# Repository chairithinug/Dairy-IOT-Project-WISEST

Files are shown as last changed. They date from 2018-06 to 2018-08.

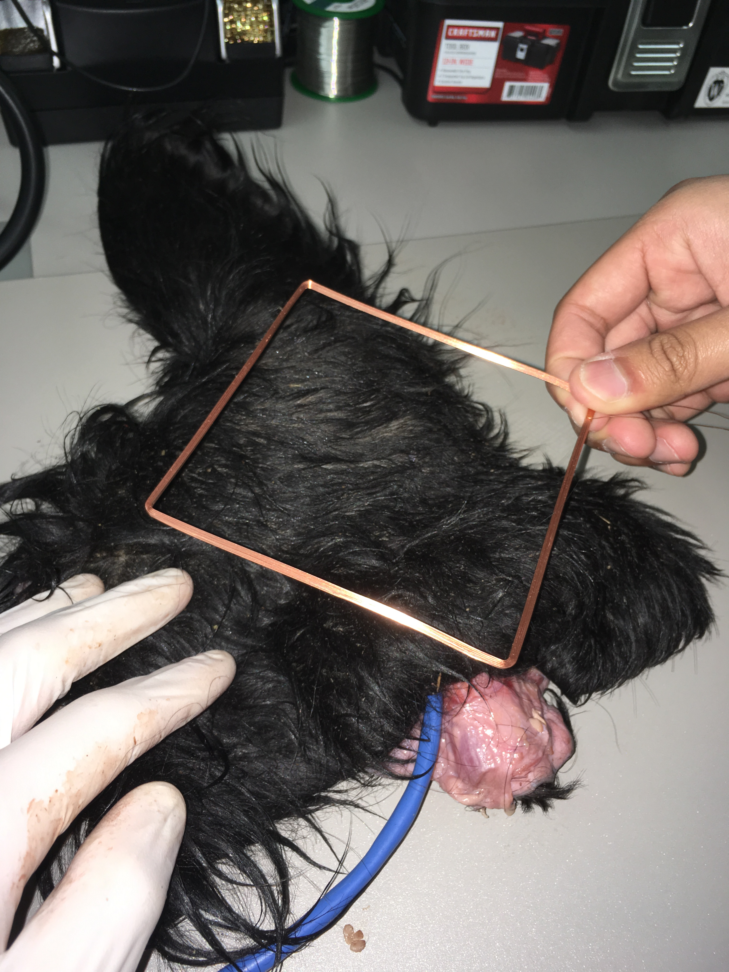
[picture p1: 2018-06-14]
Extras/IMG-1292.JPG

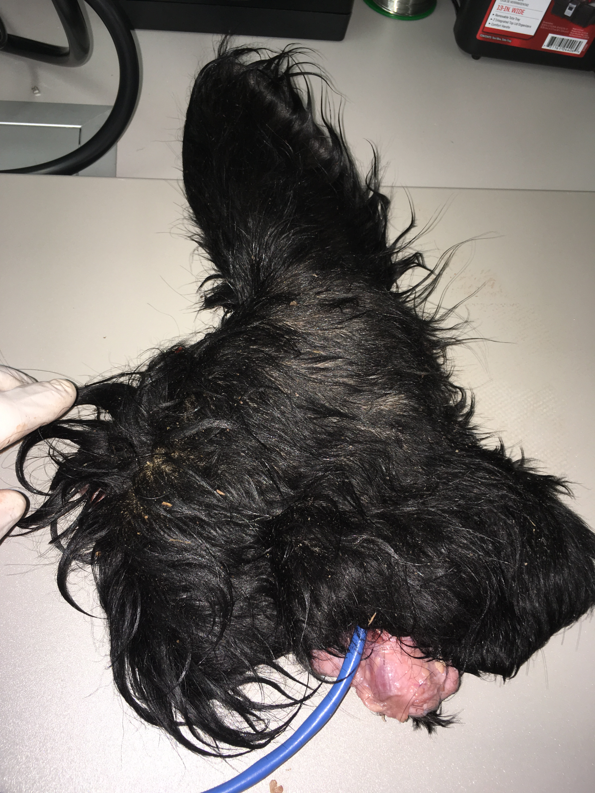
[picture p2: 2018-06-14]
Extras/IMG-1290.JPG

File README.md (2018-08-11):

# Overview
This is a private repository for my project at WISEST lab during Summer 2018 as an undergraduate research assistant. This project is a dairy IoT, using chiefly Arduino (C++/C) and MATLAB. MATLAB is responsible for gathering data from experiments and finding calibration coefficients. Arduino programs a microcontroller board. The goal is to monitor the core temperature of livestock and to wirelessly send the data through the internet.

# Components used
1. Adafruit Feather M0 LoRa MCU x2
2. ESP8266 WiFi Module
3. Priority1 RFIDRW-E-TTL Reader with an antenna
4. Bio temperature sensors
5. UBBL24-Fl-TH 7.4V 4800 mAh Batteries
6. MCP1702-3303 LDO
7. VN4012 NMOS
8. 1 uF Capacitors
9. Clipping Diodes (not used previously but recommended on RX-TX)
10. Wires
11. Prototype board
12. Header pins

# Useful electronic devices
1. Soldering station
2. Power supply
3. DMM
4. Oscilloscope

# Softwares used
1. Arduino IDE
2. Matlab R2018a
3. Altium Designer
4. Git
5. Microsoft Office
6. Google Chrome

# Libraries used
1. RH_RF95 LoRa library
2. RTCZero Timer/Low power library
3. SPI (may not actually needed)

# Codes (inside Codes folder)
1. LoRa_RX_Multi		HUB's code
2. LoRa_TX_RTC_V2		Device's code
3. LoRa_TX_NMOS			Debugging code without a sleep mode
4. Online_Matlab_Code	Thingspeak code

# Schematics
1. High-level Schematics
2. Detailed Schematics of a Hub
3. Detailed Schematics of a Device

# Useful resources
1. ESP8266 AT Command
2. Adafruit Feather M0 LoRa schematics
3. Datasheets of components
4. Some files in Extras folder

# TODO-Issue list
1. Change a number of devices connected to the hub.
2. Change a period of the reading.
3. Collision handling could be better by echoing some parts of data sent from a device to a hub back to the device.
4. Floating pin on a reader when NMOS creates an open circuit will need to be addressed. Now the current likely goes through RX-TX, which is not good.
5. There is still a grounding problem with a device and it can pick up a wrong part of data to be sent or receive a wrong data.
6. Sending all reading data to the hub might be a good idea than processing some of them on a device. This comes at a cost of power consumption.
7. Make a solid protocol between devices and a hub and across all devices.

# Words of caution when integrating parts
1. Do not connect V+ and GND of a battery. It could explode.
2. Be careful when using a DMM. Do not let a probe touch any 2 pins. This creates a short circuit.
3. Unplug or turn off a power supply first before removing any components.
4. MCU and IC are sensitive parts. Be especially careful when connecting them and notice the Vin of them.
5. When doing a hardware debugging, start at which the problem most likely happens.

# Setting up a device
1. Change period, LoRa signal power, and other variables if needed.
2. Program a device. Double-push the reset button and wait for a LED to blink, if needed.
3. Be careful when messing with Sleep mode/Standby mode of MCU. It might brick the device. 
4. In a standby mode (sleep mode), you cannot really use serial communication with a PC since the sleep mode cut the communication.
5. If needed, use LoRa_TX_NMOS to debug a device. That program does not have a sleep mode in it, while still printing a reading through a serial communication.

# Setting up a hub
1. Change a number of devices, sample per wake or other variables if needed.
2. Program a hub.
3. The LED blinks every time a hub gets any inputs.

# Setting up a Thingspeak.com
1. Create a channel that takes inputs from a hub.
2. Read data using readAPIkey and channelID.
3. Use Matlab Analysis to analyze the data.
4. Post data to a different channel using writeAPIkey and channelID.
5. Edit charts and set public view.
6. If needed, data can be exported in a CSV file.

# Charging batteries guide
1. Use a power supply and set a constant voltage (max voltage) and a constant current (1 A recommended)
2. Do not a power supply directly to a battery (for safety reason?)
3. Use a prototype board and a JST connector to create a charging device.

# Troubleshooting guide
1. Use a DMM to test a voltage at any points.
2. Use an oscilloscope to check UART communication.
3. Measure an impedance of an antenna.
4. Print out a reading and such on a serial communication.
5. Look at inputs from a hub to Thingspeak.
6. Check Thingspeak code.

# Locations of possible problems
1. Check the antenna connection.
2. Check the power connection and power level.
3. Check the software problem.
4. Check the prototype board connection.

# Final words
This project was not possible without Prof. Kim's, Jingjie's, Hanwook's and others' helps. I really appreciate all helps and advices I received and I am grateful to be given a trust to handle this project.

Contact: Anapat Chairithinugull Email: chairithinug@wisc.edu Cell: +1 6087729985

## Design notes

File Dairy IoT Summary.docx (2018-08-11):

Dairy IoT Reflection

Summer 2018

Estimated Timeline

From | To | Topic
April 14 | May 23 | Setting RFID and Arduino / Finding conversion
May 23 | June 13 | Calibrating RFID and Arduino / Checking readability
June 13 | June 20 | Setting RFID and Adafruit / Setting LoRa to LoRa
June 20 | June 27 | Setting ESP8266 / Posting data to ThingSpeak.com
June 27 | July 7 | Starting over with Priority1 RFIDRW-E-TTL
July 7 | July 12 | Optimizing power consumption
July 12 | July 19 | Reading many reader / Posting data to Thingspeak.com
July 19 | July 31 | Schematics / Finalizing components
July 31 | August 7 | Assembling
August 7 | August 10 | Experimenting / Debugging / Fixing

Part I: Setting RFID and Arduino / Finding conversion

Got assigned on a dairy IoT project with PhD student Jingjie in Prof. Kim’s Lab (WISEST). On the first day, got the reader to read data. However, spent most time fixing reading problem and understanding how to send data via serial communication. Also met Master student Hanwook.

Problem I: A RFID reader kept reading the same data even though the reset pin on RFID was used.

Solution: Used a transistor from Plexus lab (2N4401) to power on and off, with active low transistor reset (increasing source voltage).

Surprise/Learn: The use of transistor with active low (Vgs). Reset pin on RFID did nothing, or still did not understand how to use it.

Problem II: Once receive data in HEX, did not know how to convert data to temperature.

Solution: With help of JJ, found a better document from another RFID module. Check last bit of temperature zone (must be 1), BIN to HEX(ASCII), decode ASCII to HEX and then flipped and convert to DEC then divided by 10.

Surprise/Learn: See conversion in action, re-learn Matlab code.

Problem III: Leading zero got truncated by Matlab.

Solution: Wrote Arduino function that prints 0 in serial communication.

Surprise/Learn: Function in C.

Problem IV: Attempt to send HEX instead of BIN. Failed to receive correct data in Matlab.

Solution: Stick with HEX (better solution found later).

Surprise/Learn: gain more understanding of data conversion and how data is sent in serial communication.

General comment: Learn more about Arduino, serial communication, data conversion, and re-learn Matlab. Did not spend lot of time on the project due to school and exams.

Part II: Calibrating RFID and Arduino / Checking readability

Met Prof. Choi for the first time in a meeting concerning a departure of JJ for 3 weeks. Worked with Hanwook most of the time from 8-4 pm weekdays. Got a task to create a program using Matlab to collect data for calibration.

Problem I: Attempt on one of real cow’s ears without a good plan. Threw it away afterward due to the smell.

Consequence: Got warned by Prof. Choi and told to be better at planning. Spend the rest of this part working on water bags and cooking meats.

Surprise/Learn: Practice makes perfect! Good plan means better work.

Problem II: Did not have a good plan and organization to collect data.

Consequence: Had to repeat a few experiments on those earlier experiments.

Surprise/Learn: Again planning! Make a good protocol when working with others.

Problem III: Reading failed after numbers of data (10K data). Issue of zeros.

Solution: Fixed Arduino code where it stuck in a loop forever.

Surprise/Learn: Testing is the key.

Problem IV: Had no proper tools to test angle and readability.

Solution: Bought a protractor and others for measuring.

Surprise/Learn: Be more prepared.

General comment: Wrote so many Matlab codes and even create Matlab apps. However, also spent a lot of time doing experiments.

Part III: Setting RFID and Adafruit / Setting LoRa to LoRa

After the part II, Hanwook left for a break. JJ was back. Bad communication with prof. so spent a few days waiting for LoRa. Most of the time spent to understand the tutorial code of RX and TX of Feather M0 LoRa.

Problem I: Realize that SoftwareSerial cannot be used on Feather.

Solution: Went back to HardwareSerial with some buggy transitions.

Surprise/Learn: Learn the difference between HardwareSerial and SoftwareSerial and how to use them.

Problem II: IC digital voltage isolator... what is it? And how to use…? Datasheet was not friendly to a novice!

Solution: Ask for JJ’s help

Surprise/Learn: it can be used to level shift voltage.

Problem III: Burned that one IC…

Solution: Soldered a new one…

Surprise/Learn: Learn how to solder with air heat and flux of IC on a breakout board.

Problem IV: Leading zero again when sent via radio

Solution: Got all data first and send in HEX as a package.

Surprise/Learn: The reading at RX was almost perfect!

Part IV: Setting ESP8266 / Posting data to ThingSpeak.com

Tried to figure out how to use ESP8266 WiFi module. Using ThinkSpeak due to its capability to analyze by Matlab.

Problem I: ESP8266 (ESP-12e) harder to be used.

Solution: Bought ESP8266 (ESP-1)

Surprise/Learn: ESP8266 (ESP-12e) might work.

Part V: Starting over with new reader from Priority one RFIDRW-E-TTL

Since the old reader output 5V and Adafruit cannot take that. We used a new reader that outputs 3.3V.

Problem I: New reader is pre-programmed and sends only ID if not asked for more detail.

Solution: Open source code can help.

Part VI: Optimizing power consumption

No sleep for ATSAMD21 somehow. Only standby mode

Part VII: Reading many reader / Posting data to Thingspeak.com

Handle multiple inputs and collision. In the end, did not really handle a collision…

Part VIII: Schematics / Finalizing components

Draw schematics in Altium in details and high level.

Problem I: Floating Ground of a reader caused by a NMOS, resulting in higher Vin to a MCU.

Part IX: Assembling

Integrating and prototyping a device on a prototype board. Breaking some parts.

Part X: Experimenting / Debugging / Fixing

Case cracked. Wire snapped. Position moved. Data collided. With help of Prof. Kim, we all managed to get through the preliminary experiment. The antenna tends to be problematic due to its thin wire.

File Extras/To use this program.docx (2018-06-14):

# Overview

This is a private repository for my project at WISEST lab during Summer 2018 as an undergraduate research assistant. This project is a dairy IoT, using chiefly MATLAB and Arduino (C++). MATLAB is responsible for gathering data from experiments and finding calibration coefficients. Arduino programs a microcontroller board. The goal is to monitor the core temperature of livestock and to wirelessly send the data through the internet.

# Requirements

1. Arduino Uno connected to your PC via cable
2. The RFID and sensor circuit
3. The sensor
4. MATLAB 2018a (earlier versions might not support all functionalities) installed
5. MATLAB Support Package for Arduino Hardware installed and setup properly

# What these programs do

Run_Improved_V2.mlapp gathers the number of samples and displays the raw data plot and the calibrated plot. Linear regression coefficients can be applied and adjusted before the reading starts. After the reading has done, the data will be save automatically and once again before the program is closed. The LED light indicates the data availability. It becomes yellow when there is a problem with the input data, becomes red if no input data is read, turns black when the program finishes or is ready. Once data is collected, it is automatically saved to a CSV file with a timestamp.

Run_Monitoring.mlapp is similar to Run_Improved_v2.mlapp. It keeps reading data until it is stopped by users. It has an ability to breakdown data and save data into multiple files every X second specified by users. In addition to those LEDs, Run_Monitoring.mlapp has a blue LED indicating a pause. Unlike the first program, this program does NOT save when closed the program window. However, the data should be saved when “Stop” is pressed.

# How to use "Run_Improved_V2.mlapp" for known sample number

1. Connect Arduino to your PC.
2. Double-click on the program “Run_Improved_V2.mlapp”.
3. Change port name to match the port Arduino connected to. You can also check with Device Manager in your Control Panel and look for Port section.
4. Click “Connect” button to open serial communication between your PC and Arduino.
5. Adjust the number of samples you wish.
6. Check a box called “Activate” and adjust the coefficients properly, if needed.
7. Place RFID antenna close to the sensor. The LED on the RFID reader should blink, indicating that there is a data.
8. Click “Start” button when you are ready.
9. Wait until the LED turns black again.
10. If you wish to collect more data, simply click “Reset” again and press “Start”
11. Repeat step 8-10.
12. Once you are satisfied with data, close the window. Doing this prompts a dialogue block.
13. Select “Yes” if you wish to exit and save data or select “No” if you accidentally click on the close button.

# How to use "Run_Monitoring.mlapp" for monitoring

1. Connect Arduino to your PC.
2. Double-click on the program “Run_Monitoring.mlapp”.
3. Change port name to match the port Arduino connected to. You can also check with Device Manager in your Control Panel and look for Port section.
4. Click “Connect” button to open serial communication between your PC and Arduino.
5. Check a box for “save multiple files” if wish to divide data into many smaller files and specify how long in second between each file.
6. Check a box for “activate” and adjust the coefficients properly, if require calibrated data.
7. Place RFID antenna close to the sensor. The LED on the RFID reader should blink, indicating that there is data.
8. Click “Start” button when you are ready.
9. If necessary, click pause to temporarily stop the program. Note that this does not stop the timer within the program.
10. When achieve enough data as desired, click stop to stop reading and save the data.
11. If wish to collect more data, press “Start”.
12. Repeat step 8-11.
13. Once you are satisfied with data, close the window. Doing this prompts a dialogue block.
14. Select “Yes” if wish to exit or select “No” if accidentally click on the close button.

# Troubleshooting

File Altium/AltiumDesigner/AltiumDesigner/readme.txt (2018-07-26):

 

**********************************************************
*************  Important Instructions Follow  ************
**********************************************************
 
All files exported to: D:\Export_Storage\ExportBase\0\263653\Output\AltiumDesigner\AltiumDesigner\AltiumDesigner

To import your new library part into Altium follow these steps:

1. After running the Ultra Librarian export for the first time,
you will need to copy the following files into an area where
they can be accessed for all future translations.  They are script
files that Altium will need to be able to find.
	a. UL_Form.dfm
	b. UL_Form.pas
	c. UL_Import.pas
	d. UL_Import.prjScr
	
2. The above script file will need to be run from within Altium.
This can be done by going to File, Open and selecting the
UL_Import.PrjScr file stored above.

3. Select the UL_Form.pas file form the new project that has loaded,
and then select runfrom the drop down menu.  You will need to select
the form again. Run the form.

3. When the script is run, it will ask you for the file name of the
Ultra Librarian file to run.  You should select the latest file
produced with a date code if using the Ultra Librarian Free Reader
or other desktop software (for instance 2010-02-17_23-12-34.txt), or
"AltiumDesigner.txt" if using files downloaded from Ultralibrarian.com
or another online source.

4. The script will open a new Integraged Library project and import
the Ultra Librarian data into it.  When complete a message box
will pop up saying that import is done.

**************************************************************
**    !!!!!!!!!!!!!        WARNING        !!!!!!!!!!!!!     **
**************************************************************

Besure to check the documentation layer, "Mechanical 3", for important information that may seem to be missing or have not translated properly!

*** Please Note! For some styles of components, after the component has been
exported to Altium Designer, the footprint is not visible in the main library frame.
Please navigate to the PCB Library view by clicking on the "PCB Library" tab at the
bottom left side of the main library frame. Once you are in the PCB Library view,
please double click on the footprint name (which should be in the top left quadrant
of the screen). After double clicking, the footprint should appear and you should
now be able to use this footprint in your design. ***

For additional information, please visit this site:
http://www.accelerated-designs.com/help/Altium_import.html

For a video tutorial, please visit:
https://youtu.be/r1tv_wz_uY0

Ultra Librarian Gold 8.2.225 Process Report

TextStyle count:  25
Padstack count:   3
Pattern count:    3
Symbol count:     1
Component count:  1

Export

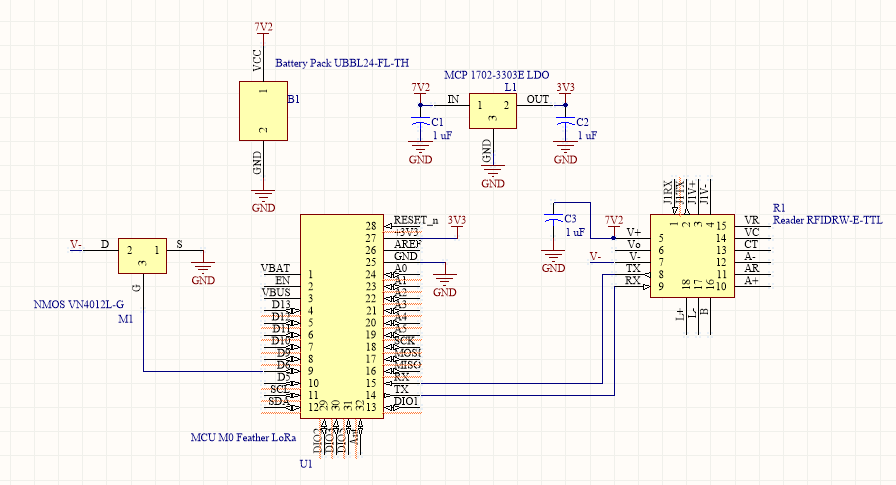
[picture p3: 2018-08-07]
Schematic_Device.PNG

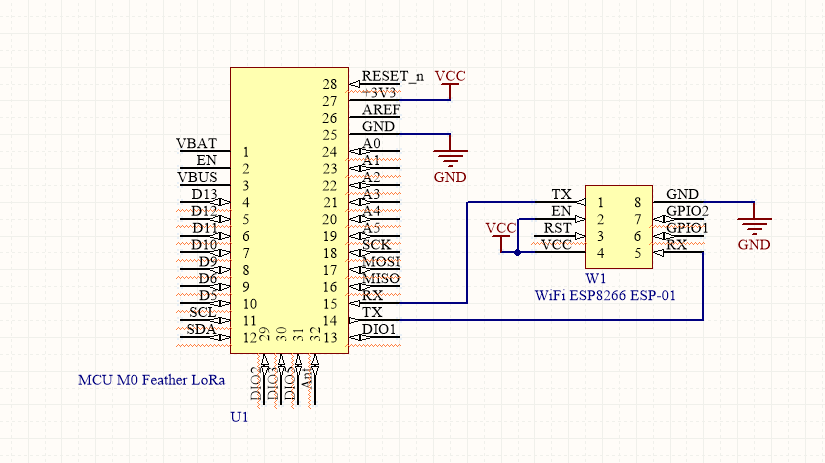
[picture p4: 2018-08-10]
Schematic_Hub.PNG

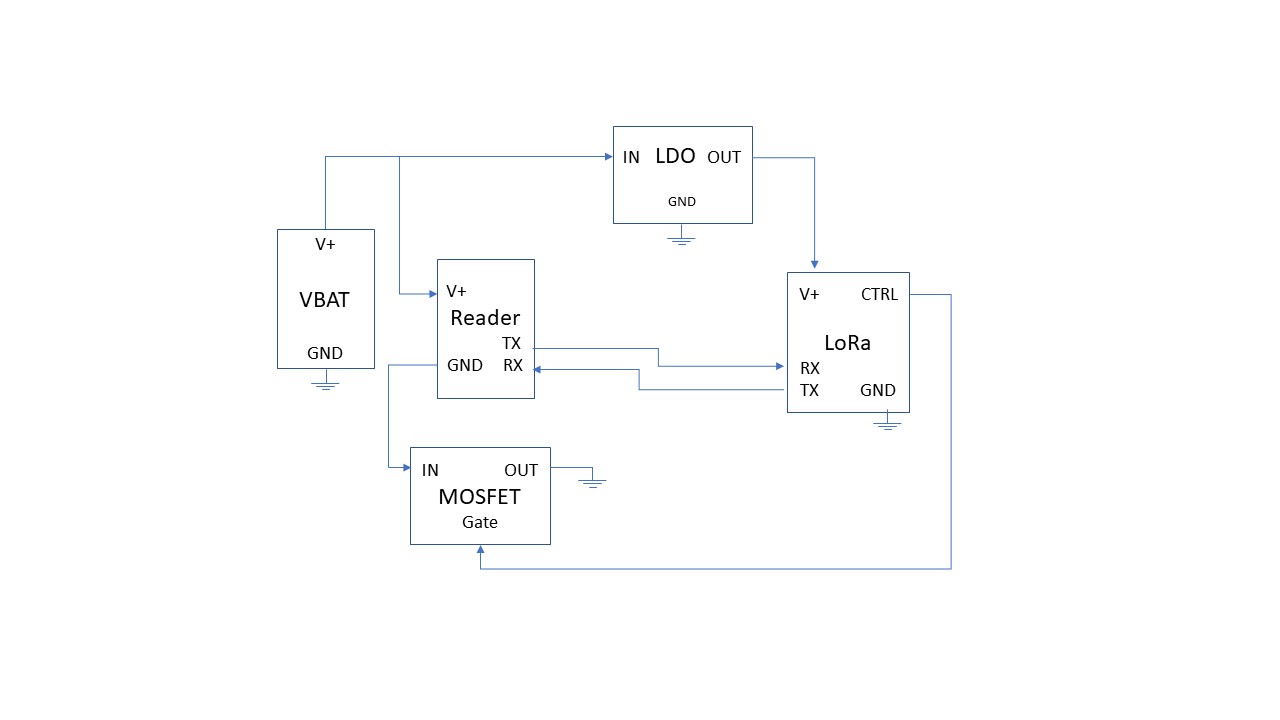
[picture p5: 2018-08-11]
High level Schematic.jpg

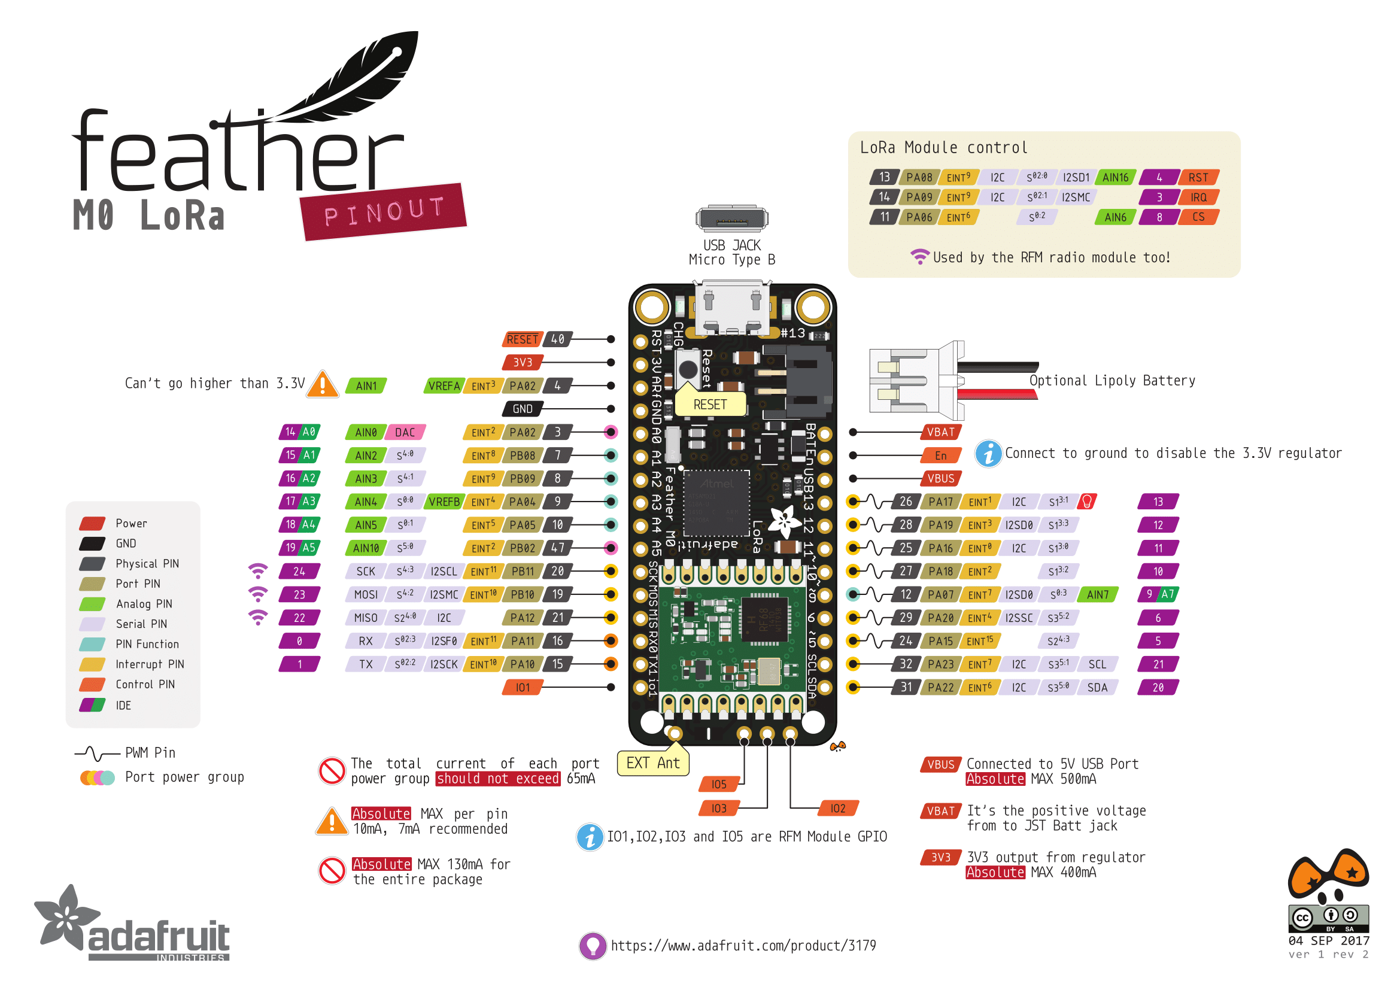
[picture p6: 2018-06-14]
Extras/feather_Feather_M0_LoRa_v1.2-1.png

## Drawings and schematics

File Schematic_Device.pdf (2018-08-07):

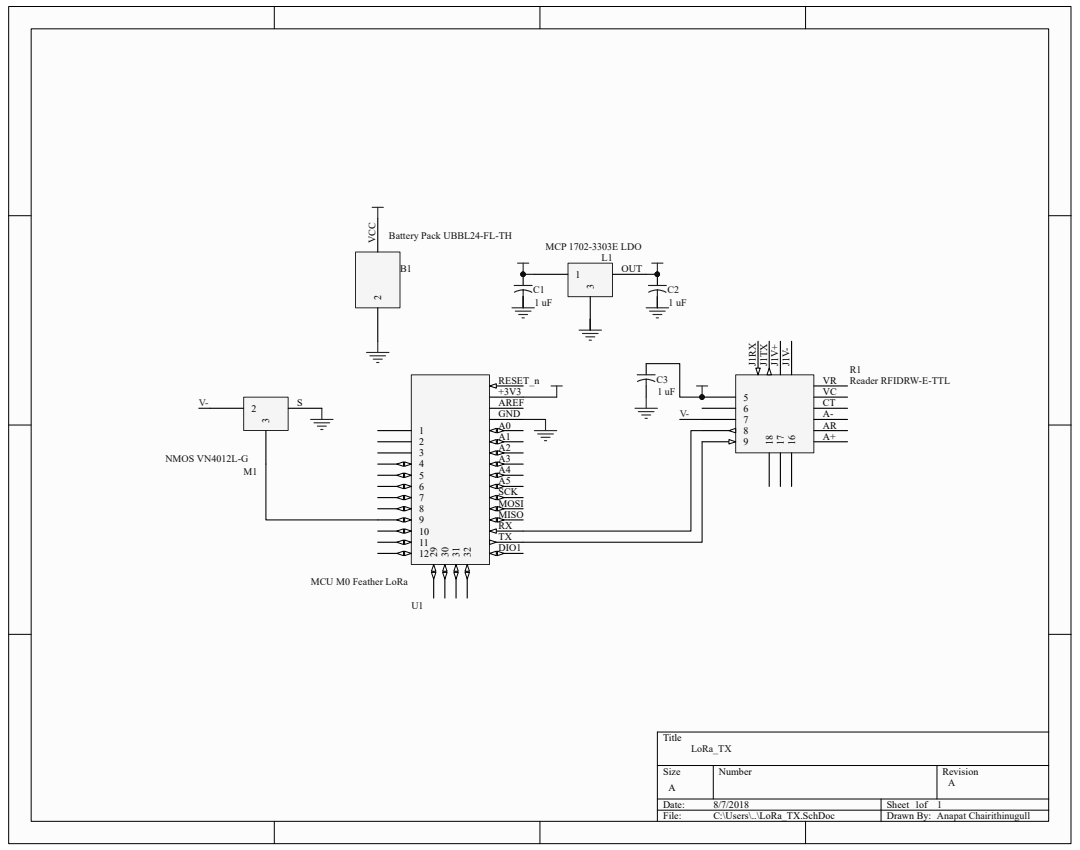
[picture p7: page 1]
Title; Size; Number; Revision; Date:; Sheet of; File:; C:\Users\..\LoRa_TX.SchDoc; Drawn By: J1RX J1TX J1V⁺ J1V-; R1 Reader RFIDRW-E-TTL; Anapat Chairithinugull; LoRa_TX; OUT; MCP 1702-3303E LDO; 1 2 3 4 5 6 7 8 9 10 11 12 DIO1; MISO; MOSI; GND; AREF; RESET_n; SCK 29303132; NMOS VN4012L-G

C2 VCC
Battery Pack UBBL24-FL-TH

MCU M0 Feather LoRa

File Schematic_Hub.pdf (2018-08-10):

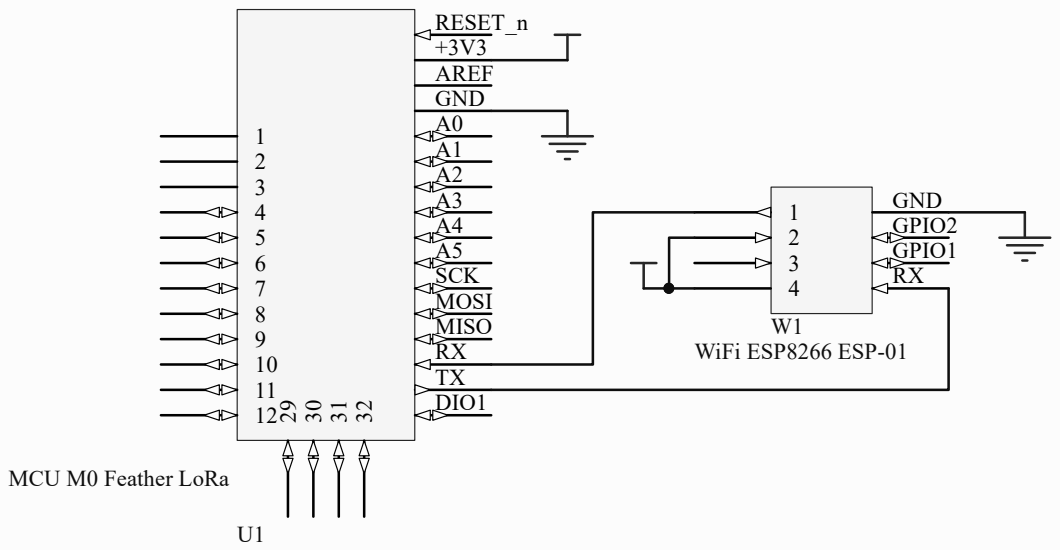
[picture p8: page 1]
Title; Size; Number; Revision; Date:; Sheet of; File:; C:\Users\..\LoRa_RX.SchDoc; Drawn By:; LoRa_RX; 1 1 Anapat Chairithinugull; 1 2 3 4 5 6 7 8 9 10 11 12 DIO1; MISO; MOSI; GND; AREF; RESET_n; SCK 29303132; GPIO1; GPIO2; W1 WiFi ESP8266 ESP-01

MCU M0 Feather LoRa

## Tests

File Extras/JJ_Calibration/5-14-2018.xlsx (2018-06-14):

Time | Data | temp 1 the next | temp 2 | temp 3 closest
2018-05-14 | 12021 | 47.8 | 47.42 | 47.29
2018-05-14 | 12022 | 47.78 | 47.4 | 47.27
2018-05-14 | 12023 | 47.77 | 47.38 | 47.26
2018-05-14 | 12024 | 47.74 | 47.36 | 47.25
2018-05-14 | 12025 | 47.72 | 47.34 | 47.23
2018-05-14 | 12026 | 47.7 | 47.34 | 47.22
2018-05-14 | 12027 | 47.68 | 47.33 | 47.22
2018-05-14 | 12028 | 47.66 | 47.33 | 47.22
2018-05-14 | 12029 | 47.66 | 47.31 | 47.22
2018-05-14 | 12030 | 47.65 | 47.3 | 47.23
2018-05-14 | 12031 | 47.65 | 47.29 | 47.22
2018-05-14 | 12032 | 47.64 | 47.28 | 47.2
2018-05-14 | 12033 | 47.63 | 47.26 | 47.19
2018-05-14 | 12034 | 47.63 | 47.25 | 47.18
2018-05-14 | 12035 | 47.63 | 47.23 | 47.17
2018-05-14 | 12036 | 47.63 | 47.22 | 47.15
2018-05-14 | 12037 | 47.64 | 47.2 | 47.14
2018-05-14 | 12038 | 47.63 | 47.19 | 47.12
2018-05-14 | 12039 | 47.61 | 47.18 | 47.12
2018-05-14 | 12040 | 47.59 | 47.16 | 47.1
2018-05-14 | 12041 | 47.58 | 47.15 | 47.09
2018-05-14 | 12042 | 47.56 | 47.13 | 47.08
2018-05-14 | 12043 | 47.55 | 47.13 | 47.07
2018-05-14 | 12044 | 47.54 | 47.11 | 47.05
2018-05-14 | 12045 | 47.52 | 47.11 | 47.04
2018-05-14 | 12046 | 47.51 | 47.1 | 47.02
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

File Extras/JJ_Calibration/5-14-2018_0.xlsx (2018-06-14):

Time | Data | temp 1 | temp 2 | temp 3
2018-05-14 | 12021 | 47.8 | 47.42 | 47.29
2018-05-14 | 12022 | 47.78 | 47.4 | 47.27
2018-05-14 | 12023 | 47.77 | 47.38 | 47.26
2018-05-14 | 12024 | 47.74 | 47.36 | 47.25
2018-05-14 | 12025 | 47.72 | 47.34 | 47.23
2018-05-14 | 12026 | 47.7 | 47.34 | 47.22
2018-05-14 | 12027 | 47.68 | 47.33 | 47.22
2018-05-14 | 12028 | 47.66 | 47.33 | 47.22
2018-05-14 | 12029 | 47.66 | 47.31 | 47.22
2018-05-14 | 12030 | 47.65 | 47.3 | 47.23
2018-05-14 | 12031 | 47.65 | 47.29 | 47.22
2018-05-14 | 12032 | 47.64 | 47.28 | 47.2
2018-05-14 | 12033 | 47.63 | 47.26 | 47.19
2018-05-14 | 12034 | 47.63 | 47.25 | 47.18
2018-05-14 | 12035 | 47.63 | 47.23 | 47.17
2018-05-14 | 12036 | 47.63 | 47.22 | 47.15
2018-05-14 | 12037 | 47.64 | 47.2 | 47.14
2018-05-14 | 12038 | 47.63 | 47.19 | 47.12
2018-05-14 | 12039 | 47.61 | 47.18 | 47.12
2018-05-14 | 12040 | 47.59 | 47.16 | 47.1
2018-05-14 | 12041 | 47.58 | 47.15 | 47.09
2018-05-14 | 12042 | 47.56 | 47.13 | 47.08
2018-05-14 | 12043 | 47.55 | 47.13 | 47.07
2018-05-14 | 12044 | 47.54 | 47.11 | 47.05
2018-05-14 | 12045 | 47.52 | 47.11 | 47.04
2018-05-14 | 12046 | 47.51 | 47.1 | 47.02
2018-05-14 | 12047 | 47.49 | 47.09 | 47
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

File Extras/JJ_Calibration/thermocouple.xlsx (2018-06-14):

temp 1 the next | temp 2 | temp 3 closest
47.8 | 47.42 | 47.29
47.78 | 47.4 | 47.27
47.77 | 47.38 | 47.26
47.74 | 47.36 | 47.25
47.72 | 47.34 | 47.23
47.7 | 47.34 | 47.22
47.68 | 47.33 | 47.22
47.66 | 47.33 | 47.22
47.66 | 47.31 | 47.22
47.65 | 47.3 | 47.23
47.65 | 47.29 | 47.22
47.64 | 47.28 | 47.2
47.63 | 47.26 | 47.19
47.63 | 47.25 | 47.18
47.63 | 47.23 | 47.17
47.63 | 47.22 | 47.15
47.64 | 47.2 | 47.14
47.63 | 47.19 | 47.12
47.61 | 47.18 | 47.12
47.59 | 47.16 | 47.1
47.58 | 47.15 | 47.09
47.56 | 47.13 | 47.08
47.55 | 47.13 | 47.07
47.54 | 47.11 | 47.05
47.52 | 47.11 | 47.04
47.51 | 47.1 | 47.02
47.49 | 47.09 | 47
47.46 | 47.08 | 46.98
47.45 | 47.07 | 46.97
47.43 | 47.05 | 46.96
47.42 | 47.04 | 46.94
47.41 | 47.02 | 46.93
47.4 | 47.02 | 46.92
47.39 | 47 | 46.9
47.38 | 46.98 | 46.88
47.37 | 46.96 | 46.87
47.35 | 46.95 | 46.85
47.33 | 46.94 | 46.84
47.31 | 46.92 | 46.82
47.29 | 46.9 | 46.81
47.28 | 46.88 | 46.79
47.26 | 46.87 | 46.78
47.25 | 46.86 | 46.77
47.24 | 46.84 | 46.76
47.23 | 46.83 | 46.75
47.22 | 46.82 | 46.74
47.21 | 46.8 | 46.73
47.2 | 46.79 | 46.72
47.19 | 46.78 | 46.71
47.18 | 46.77 | 46.71
47.16 | 46.76 | 46.7
47.16 | 46.75 | 46.69
47.15 | 46.73 | 46.67
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

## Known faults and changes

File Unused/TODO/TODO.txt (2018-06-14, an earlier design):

Linear regression (Coefficient) activate/deactivate button
2 text boxes to insert coeff.
write both data to a csv file
moving average after done.
break csv into many files (say after 10 mins)

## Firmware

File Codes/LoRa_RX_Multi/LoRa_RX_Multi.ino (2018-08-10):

#include <SPI.h>
#include <RH_RF95.h>

#define RFM95_CS 8 // Unique for Feather LoRa M0
#define RFM95_RST 4
#define RFM95_INT 3

#define RF95_FREQ 915.0 // Must be the same for RX-TX
RH_RF95 rf95(RFM95_CS, RFM95_INT);

#define LED 13 // On-board LED
#define NUMBER_OF_DEVICES 2 //TODO
#define DATA_LENGTH 18
#define ID_LENGTH 15

// Use String for the sake of ease
String AP = "UWNet"; // Need to register MAC address first (UWNet Only)
String PASS = "";
String API = "I3N8WV2Z2SV5C3EW"; // ThingSpeak.com Write API
String HOST = "api.thingspeak.com";
String PORT_NET = "80";
String field1 = "field1";

int count_command = 0;
int command_time = 0;
boolean found = false;
uint8_t buf[RH_RF95_MAX_MESSAGE_LEN];
uint8_t ongoing_data[DATA_LENGTH * NUMBER_OF_DEVICES + 1];

char list_ID[NUMBER_OF_DEVICES * ID_LENGTH];
char ID[ID_LENGTH];
int logged_devices = 0; // When a device has valid id and is registered the first time of that iteration
int bad_devices = 0; // When a device does not have a valid id, or a device fails
char OUT[2] = "1"; // A response to a sender
int comm_count = 0; // Used as a timeout.

void setup()
{
  device_init();
}

void loop()
{
  if (rf95.available()) {
    transmit(OUT, sizeof(OUT)); // signal that it received data
    digitalWrite(LED, HIGH);
    uint8_t len = sizeof(buf);
    if (rf95.recv(buf, &len))
      Serial.println((char*) buf);
    else
      Serial.println("Receive failed");

    strncpy(ID, (char*) buf, 15); // copy the ID to be compared
    Serial.print("This ID is ");
    Serial.println(ID);

    if (!is_repeated_ID(ID, logged_devices)) {
      Serial.print(ID);
      Serial.println(" logged");
      Serial.println();
      memcpy(list_ID + logged_devices * ID_LENGTH, ID, ID_LENGTH); // Add this ID to a list

      memcpy(ongoing_data + logged_devices * DATA_LENGTH, buf, DATA_LENGTH); // Attach this data to a package
      logged_devices++;
    }

    comm_count++;
    memset(&ID[0], 0, sizeof(ID)); // Clear memory with null
    delay(100);
    digitalWrite(LED, LOW);
  }
  if (logged_devices + bad_devices >= NUMBER_OF_DEVICES || comm_count > 2 * NUMBER_OF_DEVICES) { //comm_count is a timeout condition
    Serial.print("sending data from ");
    Serial.print(logged_devices);
    Serial.print(" out of ");
    Serial.print(NUMBER_OF_DEVICES);
    Serial.println(" devices");
    Serial.print((char*) ongoing_data);
    Serial.println();
    post2API();
    logged_devices = 0;
    comm_count = 0;
    memset(&ongoing_data[0], 0, sizeof(ongoing_data)); // Clear memory with null
    memset(&list_ID[0], 0, sizeof(list_ID));
  }
}

/////////////////////////////////////////////////////////////////////////////////
// Setup the program
/////////////////////////////////////////////////////////////////////////////////

void device_init() {
  radio_init();
  Serial.begin(115200);
  Serial1.begin(115200);
  wifi_init();
  memset(&buf[0], 0, RH_RF95_MAX_MESSAGE_LEN); // Clear memory with null
  memset(&ongoing_data[0], 0, sizeof(ongoing_data));
  memset(&list_ID[0], 0, sizeof(list_ID));
  memset(&ID[0], 0, sizeof(ID));
  digitalWrite(LED, LOW);
}

/////////////////////////////////////////////////////////////////////////////////
// Setup LoRa communication
/////////////////////////////////////////////////////////////////////////////////

void radio_init() {
  pinMode(LED, OUTPUT);
  pinMode(RFM95_RST, OUTPUT);
  // manual reset
  digitalWrite(RFM95_RST, LOW);
  delay(10);
  digitalWrite(RFM95_RST, HIGH);
  delay(10);
  while (!rf95.init())
    while (1);
  if (!rf95.setFrequency(RF95_FREQ))
    while (1);
  rf95.setTxPower(23, false);
}

/////////////////////////////////////////////////////////////////////////////////
// Setup WiFi module
/////////////////////////////////////////////////////////////////////////////////

void wifi_init() {
  send_command("AT", 5, "OK"); // Check ESP8266
  send_command("AT+CWMODE=1", 5, "OK"); // Set station mode
  send_command("AT+CWJAP=\"" + AP + "\",\"" + PASS + "\"", 20, "OK"); // Connect to WiFi
}

/////////////////////////////////////////////////////////////////////////////////
// (ESP8266) send command and wait for expected reply before timeout
// Parameters
//            command: AT command to ESP8266
//            max_time: a timeout
//            read_reply: an array of expected data from ESP8266
/////////////////////////////////////////////////////////////////////////////////

void send_command(String command, int max_time, char read_reply[]) {
  Serial.print(count_command);
  Serial.print(". ");
  Serial.print(command);
  Serial.print(" ");
  while (command_time < (max_time * 1))
  {
    Serial1.println(command); // AT+CIPSEND
    Serial.write(Serial1.read());
    if (Serial1.find(read_reply)) // OK
    {
      found = true;
      break;
    }
    command_time++;
  }
  if (found == true)
  {
    Serial.println("OK");
    count_command++;
    command_time = 0;
  }
  if (found == false)
  {
    Serial.println(" Fail");
    count_command = 0;
    command_time = 0;
  }
  found = false;
}

/////////////////////////////////////////////////////////////////////////////////
// Request an update to Thingspeak
/////////////////////////////////////////////////////////////////////////////////

void post2API() {
  String getData = "GET /update?api_key=" + API + "&" + field1 + "=x" + String((char*) ongoing_data);// Add x to be considered string in Matlab.
  send_command("AT+CIPMUX=1", 20, "OK"); // Multiple connection
  send_command("AT+CIPSTART=0,\"TCP\",\"" + HOST + "\"," + PORT_NET, 15, "OK"); // Establish TCP
  send_command("AT+CIPSEND=0," + String(getData.length() + 50), 4, ">"); // Set data length
  Serial1.println(getData);
  send_command("AT+CIPCLOSE=0", 5, "OK"); // Close TCP
  Serial.println();
}

/////////////////////////////////////////////////////////////////////////////////
// Check if this ID has been logged already
// Parameters
//            ID: a pointer to the ID of a new device
//            logged_devices: a number of devices that have been logged previously
/////////////////////////////////////////////////////////////////////////////////

boolean is_repeated_ID(char* ID, int logged_devices) {
  for (int i = 0; i < logged_devices; i++) {
    Serial.print("comparing ");
    Serial.print(ID);
    Serial.print(" and ");
    Serial.println((list_ID + i * ID_LENGTH));
    if (strncmp((char*) (list_ID + i * ID_LENGTH), ID, ID_LENGTH) == 0) {
      Serial.println("This ID has already logged");
      Serial.println();
      return true;
    }
  }
  return false;
}

/////////////////////////////////////////////////////////////////////////////////
// Send data to the hub using LoRa
// Parameters
//            sendpacket: a pointer of a data array
//            LENGTH: a number of characters to be sent
/////////////////////////////////////////////////////////////////////////////////

void transmit(char sendpacket[], int LENGTH) {
  Serial.println("Replying someone");
  rf95.send((uint8_t *)sendpacket, LENGTH);
  rf95.waitPacketSent();
}

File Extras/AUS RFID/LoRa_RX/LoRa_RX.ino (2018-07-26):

#include <SPI.h>
#include <RH_RF95.h>

#define RFM95_CS 8 // Unique for Feather LoRa M0
#define RFM95_RST 4
#define RFM95_INT 3

#define RF95_FREQ 915.0 // Must be the same for RX-TX
RH_RF95 rf95(RFM95_CS, RFM95_INT);

#define LED 13 // On-board LED

String AP = "UWNet"; // Need to register MAC address first (UWNet Only)
String PASS = "";
String API = "I3N8WV2Z2SV5C3EW"; // ThingSpeak.com Write API
String HOST = "api.thingspeak.com";
String PORT_NET = "80";
String field1 = "field1";
String field2 = "field2";

int count_command = 0;
int command_time = 0;
boolean found = false;
uint8_t buf[RH_RF95_MAX_MESSAGE_LEN];

void setup()
{
  radio_init();
  Serial.begin(115200);
  Serial1.begin(115200);
  wifi_init();
  memset(&buf[0], 0, RH_RF95_MAX_MESSAGE_LEN); // Clear memory with null
  digitalWrite(LED, LOW);
}

void loop()
{
  if (rf95.available())
  {
    digitalWrite(LED, HIGH);
    uint8_t len = sizeof(buf);
    if (rf95.recv(buf, &len))
      Serial.println((char*) buf);
    else
      Serial.println("Receive failed");
z
    post2API();
    delay(100);
    digitalWrite(LED, LOW);
  }
}

void radio_init() {
  pinMode(LED, OUTPUT);
  pinMode(RFM95_RST, OUTPUT);
  // manual reset
  digitalWrite(RFM95_RST, LOW);
  delay(10);
  digitalWrite(RFM95_RST, HIGH);
  delay(10);
  while (!rf95.init())
    while (1);
  if (!rf95.setFrequency(RF95_FREQ))
    while (1);
  rf95.setTxPower(23, false);
}

void wifi_init() {
  sendCommand("AT", 5, "OK"); // Check ESP8266
  sendCommand("AT+CWMODE=1", 5, "OK"); // Set station mode
  sendCommand("AT+CWJAP=\"" + AP + "\",\"" + PASS + "\"", 20, "OK"); // Connect to WiFi
}

// (ESP8266) send command and wait for expected reply before timeout
void sendCommand(String command, int maxTime, char readReplay[]) {
  Serial.print(count_command);
  Serial.print(". ");
  Serial.print(command);
  Serial.println(" ");
  while (command_time < (maxTime * 1))
  {
    Serial1.println(command); // AT+CIPSEND
    if (Serial1.find(readReplay)) // OK
    {
      found = true;
      break;
    }
    command_time++;
  }
  if (found == true)
  {
    count_command++;
    command_time = 0;
  }
  if (found == false)
  {
    Serial.println("Fail");
    count_command = 0;
    command_time = 0;
  }
  found = false;
}

void post2API() {
  String getData = "GET /update?api_key=" + API + "&" + field1 + "=x" + String((char*) buf) + "&" + field2 + "=" + rf95.lastRssi(); // Add x at the beginning so that it is considered string in Matlab table.
  sendCommand("AT+CIPMUX=1", 5, "OK"); // Multiple connection
  sendCommand("AT+CIPSTART=0,\"TCP\",\"" + HOST + "\"," + PORT_NET, 15, "OK"); // Establish TCP
  sendCommand("AT+CIPSEND=0," + String(getData.length() + 4), 4, ">"); // Set data length
  Serial1.println(getData);
  sendCommand("AT+CIPCLOSE=0", 5, "OK"); // Close TCP
}

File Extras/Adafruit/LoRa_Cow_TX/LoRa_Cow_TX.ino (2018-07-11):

#include <SPI.h>
#include <RH_RF95.h>

#define RFM95_CS 8 // Unique for Feather LoRa M0
#define RFM95_RST 4
#define RFM95_INT 3

#define RF95_FREQ 915.0
RH_RF95 rf95(RFM95_CS, RFM95_INT);

#define RST_POW 6 // Reset transistor to keep reading
#define RST_READER 5 // Reset reader always HIGH
#define DATA_NUM 30 // Number of bytes receieved from sensor
#define LED 13
#define PERIOD 1// how long roughly (second) between two reading

#define VBATPIN A7 // Pin 9 (analog 7)

const int PACKET_LENGTH = 2 * DATA_NUM;
const int HALF_PERIOD = PERIOD * 1000 / 2;

byte data_read, data_shift;
int shift_count = 0;
int index_byte = 0;
char packet[PACKET_LENGTH] = {};

void setup()
{
  Serial.begin(115200);
  delay(100);
  radio_init();

  Serial1.begin(9600);
  reader_init();
  Serial1.flush();
  memset(&packet[0], 0, sizeof(packet)); // initialize memory with null
}

void loop()
{
  digitalWrite(LED, LOW);
  if (Serial1.available() > 0) {
    data_read = Serial1.read();
    if ((data_read == 2 && index_byte == 0) || index_byte != 0) // for the first 2
    {
      sprintf(packet + index_byte * 2, "%0.2x", data_read);
      index_byte = index_byte + 1;
    }
    else
      index_byte = 0;
  }
  if (index_byte >= DATA_NUM) {
    printPacket(packet, PACKET_LENGTH);
    digitalWrite(LED, HIGH);
    Serial1.end();
    battery_level();
    transmit(packet, PACKET_LENGTH);
    memset(&packet[0], 0, sizeof(packet)); // clear memory with null
    index_byte = 0;
    digitalWrite(RST_POW, HIGH);
    delay(HALF_PERIOD);
    digitalWrite(RST_POW, LOW);
    Serial1.begin(9600);
    Serial1.flush();
    delay(HALF_PERIOD);
    digitalWrite(LED, LOW);
  }
}

void radio_init() {
  pinMode(RFM95_RST, OUTPUT);
  digitalWrite(RFM95_RST, HIGH);
  Serial.println("Feather LoRa TX Test!");
  // Manual reset
  digitalWrite(RFM95_RST, LOW);
  delay(10);
  digitalWrite(RFM95_RST, HIGH);
  delay(10);
  while (!rf95.init()) {
    Serial.println("LoRa failed");
    while (1);
  }
  Serial.println("LoRa OK!");
  // Defaults after init are 434.0MHz, modulation GFSK_Rb250Fd250, +13dbM
  if (!rf95.setFrequency(RF95_FREQ)) {
    Serial.println("setFrequency failed");
    while (1);
  }
  Serial.print("Freq: ");
  Serial.println(RF95_FREQ);
  // Defaults after init are 434.0MHz, 13dBm, Bw = 125 kHz, Cr = 4/5, Sf = 128chips/symbol, CRC on
  // The default transmitter power is 13dBm, using PA_BOOST.
  // If you are using RFM95/96/97/98 modules which uses the PA_BOOST transmitter pin, then
  // you can set transmitter powers from 5 to 23 dBm:
  rf95.setTxPower(23, false);
}

void reader_init() {
  pinMode(RST_POW, OUTPUT);
  pinMode(RST_READER, OUTPUT);
  pinMode(LED, OUTPUT);
  digitalWrite(RST_POW, HIGH);
  delay(10);
  digitalWrite(RST_POW, LOW);
  delay(10);
  digitalWrite(RST_READER, HIGH);
}

void battery_level() {
  float vbat = analogRead(VBATPIN);
  vbat *= 2;    // we divided by 2, so multiply back
  vbat *= 3.3;  // Multiply by 3.3V, our reference voltage
  vbat /= 1024; // convert to voltage
  Serial.print("Battery: ");
  Serial.println(vbat);
}

void transmit(char packet[], int PACKET_LENGTH) {
  Serial.print("Sending ");
  Serial.println(packet);
  delay(10);
  rf95.send((uint8_t *)packet, PACKET_LENGTH);
  delay(10);
  rf95.waitPacketSent();
}

void printPacket(char packet[], int packet_len) {
  for (int i = 0 ; i < packet_len; i++) {
    Serial.print(packet[i]);
    Serial.print("(");
    Serial.print(i);
    Serial.print(") ");
  }
  Serial.println("");
}

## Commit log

2018-05-27 create a new version of mlapp
    [Readings 2018-05-27-16-14-03.csv, Readings 2018-05-27-16-26-22.csv, Readings 2018-05-27-16-29-09.csv, Readings 2018-05-27-16-29-46.csv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]
2018-05-28 Add 2nd plot on graph and add reset button and misc fix
    [5-28-2018_sensor1_distance.xlsx, 5-28-2018_sensor1_distance_cup.xlsx, Combined_Distance.xlsx, Combined_Distance_Water.xlsx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]
2018-05-30 Added dim button after start and fix data saved that did not actually save and added fclose
    [5-29-2018_sensor2_t.xlsx, 5-29-2018_sensor3_t.xlsx, 5-29-2018_sensor5_t.xlsx, 5-30-2018_sensor1_t.xlsx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]
2018-06-02 Reorganize files and extract only important ones. Add error reporting script and rename Post_Report_Run.m
    [5-30-2018_sensor1b_t.xlsx, 5-31-2018_sensor2_t.xlsx, 5-31-2018_sensor4_t.xlsx, 5-31-2018_sensor5_t.xlsx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]
2018-06-03 Added new monitoring program and fix an issue with app.s
    [Readings 2018-05-26-17-08-46.csv, Readings 2018-05-26-17-27-44.csv, Readings 2018-05-26-17-28-53.csv, Readings 2018-05-26-17-29-32.csv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]
2018-06-03 removes unused files
    [Readings 2018-06-02-16-50-20.csv, Readings 2018-06-02-16-51-07.csv, Readings 2018-06-02-16-53-47.csv, Readings 2018-06-02-17-18-40.csv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]
2018-06-03 Reorganize file locatiosn
    [5-23-2018.xlsx, 5-23-2018_2.xlsx, 5-24-2018.xlsx, 5-25-2018 (Sensor 1) (1).xlsx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]
2018-06-03 Another reorganization and renaming folders
    [5-14-2018.xlsx, 5-14-2018_0.xlsx, 5-23-2018.xlsx, 5-23-2018_2.xlsx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]
2018-06-06 After Ear Experiment
    [Readings 2018-06-03-13-05-34.csv, Readings 2018-06-03-13-37-53.csv, Readings 2018-06-03-14-23-03.csv, Readings 2018-06-03-16-27-02.csv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]
2018-06-10 Added autosave
    [Readings 2018-06-07-14-41-58.csv, Readings 2018-06-07-14-47-21.csv]
2018-06-12 Added newer version of Arduino code that transmits all data as a packet of 30 data in HEX after 30 data is received and add a matlab script that reads HEX and convert to Temp
2018-06-14 From Lab PC with edited rf_temp, monitoring data, and Adafruit programs
    [5-14-2018.xlsx, 5-14-2018_0.xlsx, 5-23-2018.xlsx, 5-23-2018_2.xlsx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]
2018-06-14 Added last data
    [Part41 Readings 2018-06-13-20-55-25.csv, Part42 Readings 2018-06-13-20-55-25.csv]
2018-06-17 Added data and Adafruit rf temp program
    [Part1 Readings 2018-06-16-19-04-19.csv]
2018-06-17 Adafruit rf temp added
    [Part1 Readings 2018-06-16-19-07-50.csv]
2018-06-18 with kinda work wireless connection
2018-07-01 functions in RX TX and Added power data and sleep stuff
    [Power Data.xlsx]
2018-07-07 Added codes for new RFID
    [Power Data.xlsx]
2018-07-11 Added EnergySaving lib and code
    [Data Translation.xlsx]
2018-07-16 Added a battery voltage and xxxxxxxxxx for no reader response
2018-07-20 Added some Altium files
    [Modules.SchLib, Sheet1.SchDoc]
2018-07-26 Added Multi-device reading code and changed Period to 30 sec
2018-07-26 Added Altium files (Schematic)
    [AltiumDesigner.PcbLib, AltiumDesigner.SchLib, LoRa_RX.SchDoc, LoRa_TX.SchDoc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]
2018-07-26 Edited Schematic
    [LoRa_RX.SchDoc, LoRa_TX.SchDoc]
2018-07-27 Updated Schematics
    [LoRa_TX.SchDoc, Modules.SchLib]
2018-07-28 updated schematic
    [LoRa_TX.SchDoc, Modules.SchLib]
2018-08-04 Added reading 3 samples each round and average them and added listener on TX
2018-08-07 Edit schematics and add PDF and JPG of it
    [LoRa_TX.SchDoc]
2018-08-10 Commented and edited transmitter code. Reorganized files and added documentation (partly done)
    [5-14-2018.xlsx, 5-14-2018_0.xlsx, 5-23-2018.xlsx, 5-23-2018_2.xlsx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]
